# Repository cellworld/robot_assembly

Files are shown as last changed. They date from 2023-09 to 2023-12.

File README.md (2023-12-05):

# Assembly Instructions 

<!-- ![Alt Text](https://github.com/cellworld/robot_assembly/blob/master/robot_overview.png) -->
<p align="center">
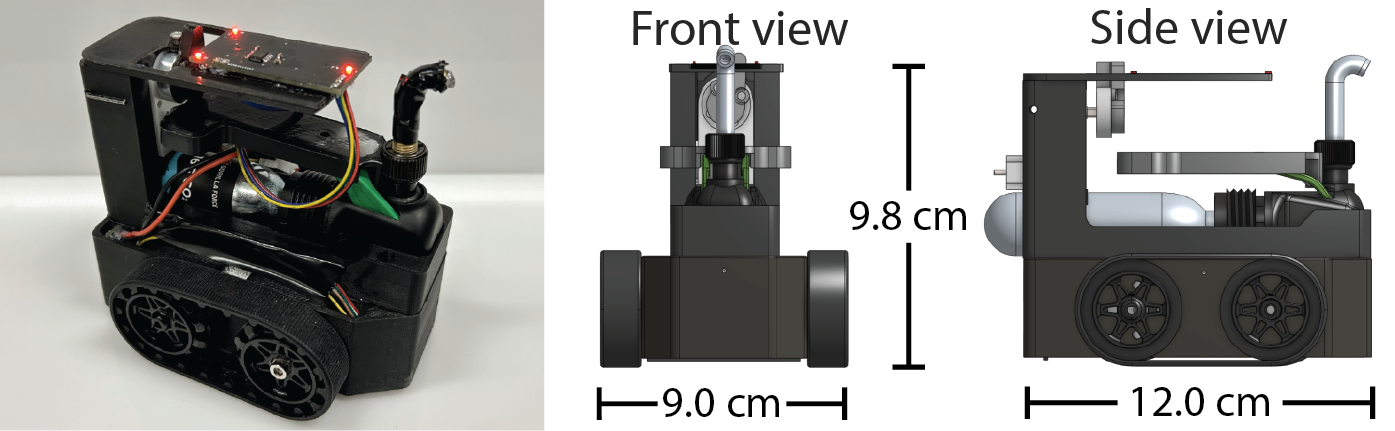
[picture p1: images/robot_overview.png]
robot_overview
  
</p>

## 3D printed parts
* chassis.stl 
* pump_holder.stl
* motor_stopper.stl
* motor_platform.stl
* lever_arm.stl
* cam.stl

## Robot and aversive puff parts
* **Plastic gearmotor** (Gearmotor and Encoder Assembly for Romi/TI-RSLK MAX, Pololu, Las Vegas, Nevada, USA, part no. 3675)
* **Motor shaft adapter** ( Pololu Universal Aluminum Mounting Hub for 3mm Shaft, M3 Holes (2-Pack), Pololu, Las Vegas, Nevada, USA, part no. 1996)
* **Valve stem extender** (2-Pack Tire Valve Extension 45 Degree, LEEGAWU)
* **16g CO2 canister and inflator** (Ultraflate, Genuine Innovations, San Luis Obispo, CA, USA)
* **Drivetrain motor** (Geared DC Motor with Magnetic Encoder Outputs - 7 VDC 1:20 Ratio, Adafruit, New York, NY, USA, part no. 4416)
* **Battery** 7.4V (7.4V 1000mAh Odamiya Plug Lithium Battery, PUOO)
* **Track set** (Pololu 22T Track Set - Black, Pololu, Las Vegas, Nevada, USA, part no. 3030)

## Printed circuit board (PCB) components
<!-- maybe add actual photo of assembled pcbs-->
<p align="center">
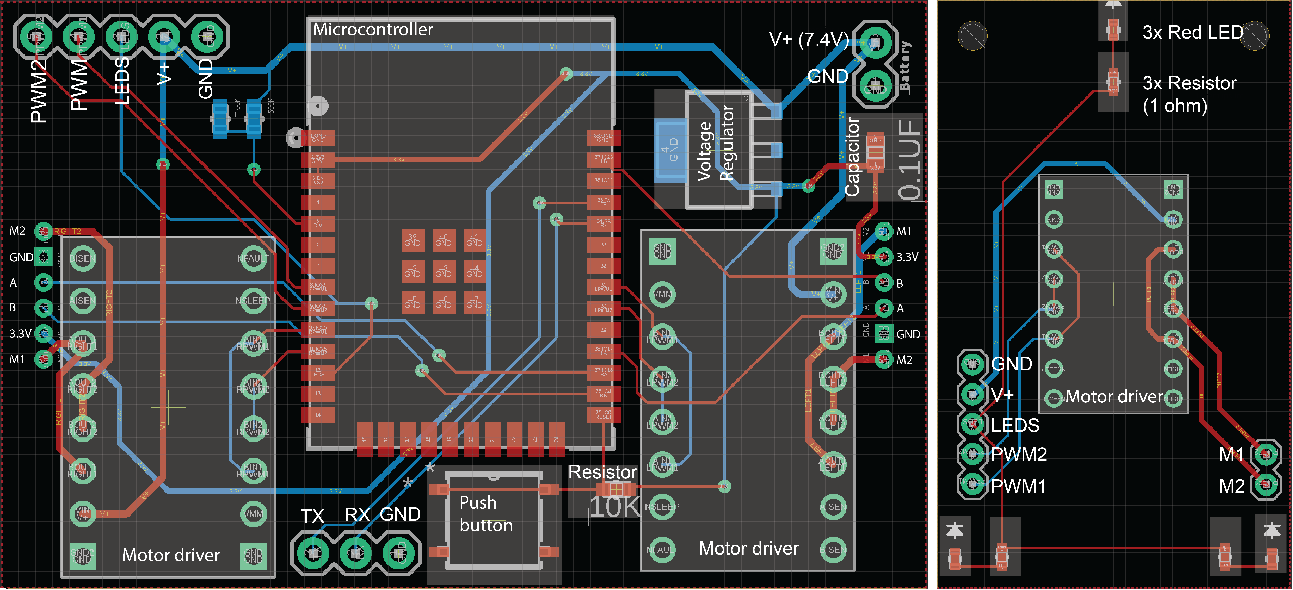
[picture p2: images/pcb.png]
pcb
  
</p>

* **Microcontroller** (ESP32-WROOM-32D, Espressif Systems, Shanghia, Shanghai, China)
* **Motor driver** ( DRV8833 Dual Motor Driver Carrier, Pololu, Las Vegas, Nevada, USA, part no. 2130)
* **Voltage regualtor** (IC REG LIN 3.3V 500MA SOT223-4, Texas Instruments, Dallas, TX, USA, Digi-key part no. 296-13424-1-ND)
* **Resistor** $10K \Omega$ (RES SMD 10K OHM 5% 1/10W 0603)
* **Capacitor** $0.1 \mu F$ (0.1 µF ±20% 50V Ceramic Capacitor X7R 0603 (1608 Metric))
* **Push button** (TACT 5.2 X 5.2, 1.5 MM H, 260GF, C&K, Digi-key part no. CKN12221-6-ND)
* **Red LED** (SMD 0603 (1.6mm x 0.8mm) Red LED Diode, Chanzon)
* **Resistor** $1 \Omega$ (RES 1 OHM 5% 1/4W 0402)
* **Drivetrain motor cable** (6 CIRC PICOBLADE RECP:PLUG 150MM, Molex, Lisle, IL, USA, Digi-key part no. 	900-2181130601-ND)
* **Plastic gearmotor cable** (JUMPER WIRE 0.1" 2-PIN 6", SparkFun Electronics, Niwot, CO, USA, Digi-key part no. 1568-1929-ND)
* **PCB connection cable** (JUMPER WIRE 0.1" 5-PIN 6", SparkFun Electronics, Niwot, CO, USA, Digi-key part no. 1568-1932-ND)

## PCB Assembly
This PCB was design using EAGLE. It is PCB CAD software. EAGLE is available from Autodesk either as part of the Fusion 360 software package or you can a free version of just EAGLE [here](https://www.autodesk.com/products/eagle/free-download). The EAGLE project, associated library, and gerber files are located in the pcb directory [here](https://github.com/cellworld/robot_assembly/tree/master/pcb/).

## Chassis assembly
<p align="center">
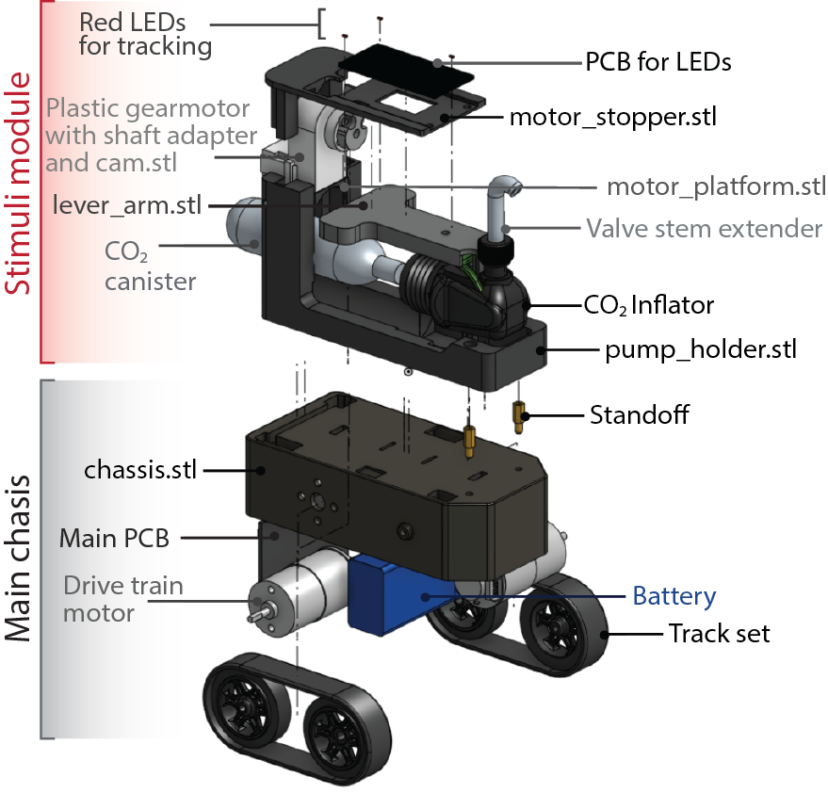
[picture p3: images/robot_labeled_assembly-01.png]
labeled robot
  
</p>

### Main chassis
1. Attach the two ABS idler sprockets from the *track set* to *chassis.stl* with a M3 shoulder bolt with a 5mm threaded portion, a washer, and a bolt.
2. Mount two *drivetrain motors*  to *chassis.stl* with M3 screws
3. Attach the two ABS drive sprockets to the *drivetrain motor* shafts
4. Attach the two silicone tracks
5. Insert the *main PCB* into the back of the *chassis.stl* and connect it to the *drivetrain motors*
6. Insert the *battery* and connect it to the *main pcb*
   
### Stimuli module 
1. Insert two M3 standoffs into the two front through holes in *chassis.stl*
2. Press fit the *pump_holder.stl* onto the standoffs
3. Add the *16g CO2 canister and inflator*  with *lever_arm.stl* press fit onto it
4. Slide components into the back channel on the  *pump_holder.stl*:
   1. *motor_platform.stl*, so that its rounded surface rests against the CO2 canister
   2. *plastic gearmotor* (with *cam.stl*  fixed to it with the *motor shaft adapter*)
   3. *motor_stopper.stl* 
5. Fix the PCB with LEDs on it to the top of the *motor_stopper.stl* and connect it to the *main PCB* and the *plastic gearmotor*
   
# Code
Relevant code for the robot resides in separate repositories.
* OTA programming code: [Link](https://github.com/cellworld/ESP32_OTA_programmer)
* Embedded code for BotEvade task: [Link](https://github.com/cellworld/robot_embedded_code/tree/b2fe92d203f52c9526e03de08260bb5708b2de43)

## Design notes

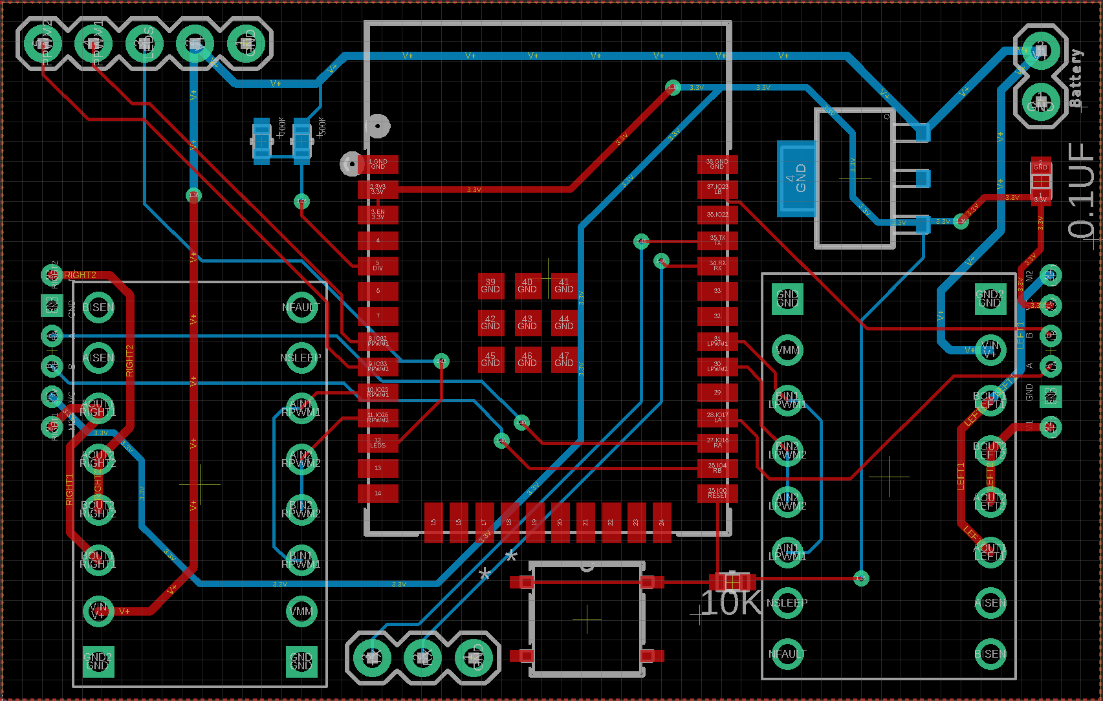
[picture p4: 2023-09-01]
images/main_pcb.png

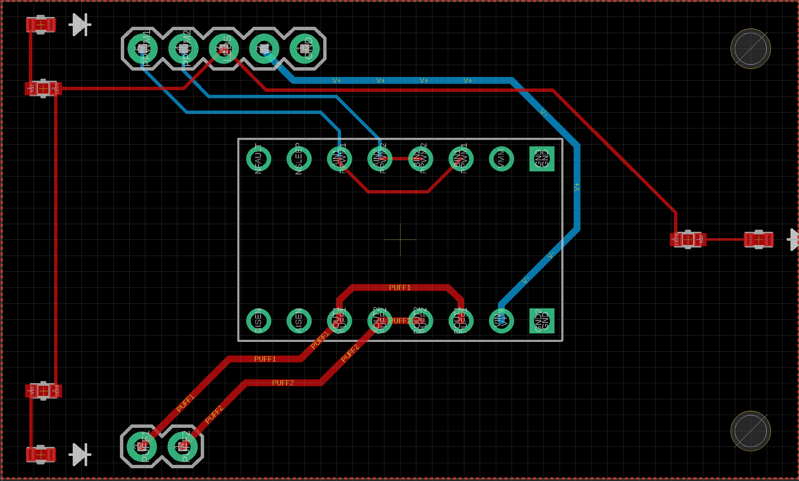
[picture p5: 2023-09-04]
images/top_pcb.png

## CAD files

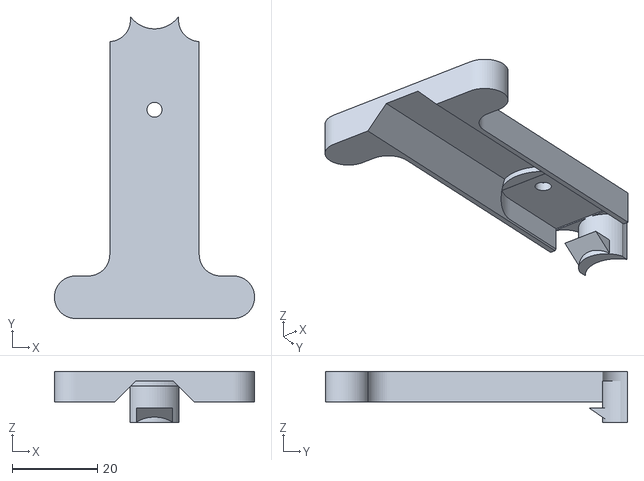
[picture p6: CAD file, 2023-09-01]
3D_printed_parts/lever_arm.stl
47.0 x 70.9 x 12.0

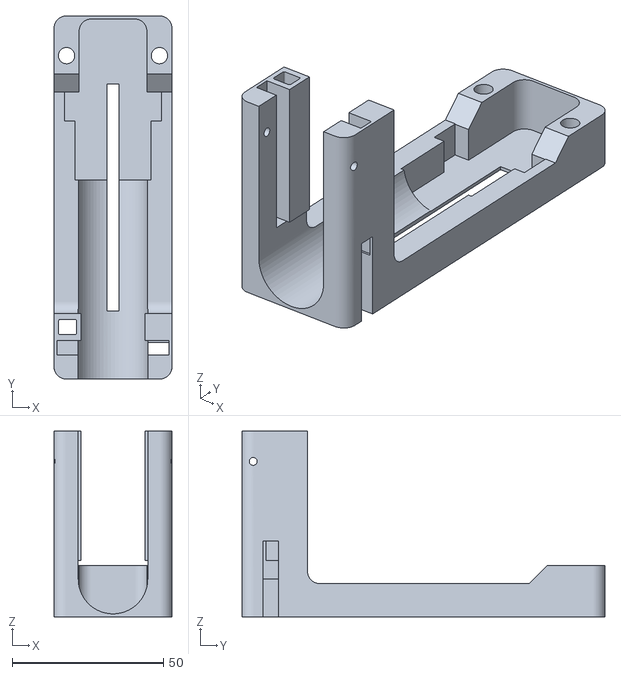
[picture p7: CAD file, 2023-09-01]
3D_printed_parts/pump_holder.stl
39.0 x 120.0 x 61.4

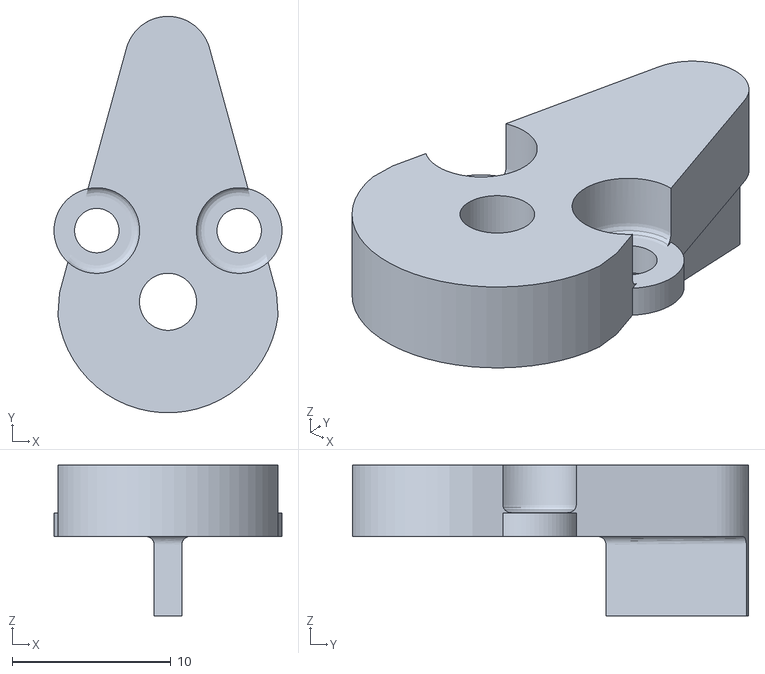
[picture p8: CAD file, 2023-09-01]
3D_printed_parts/cam.stl
14.4 x 25.0 x 9.50

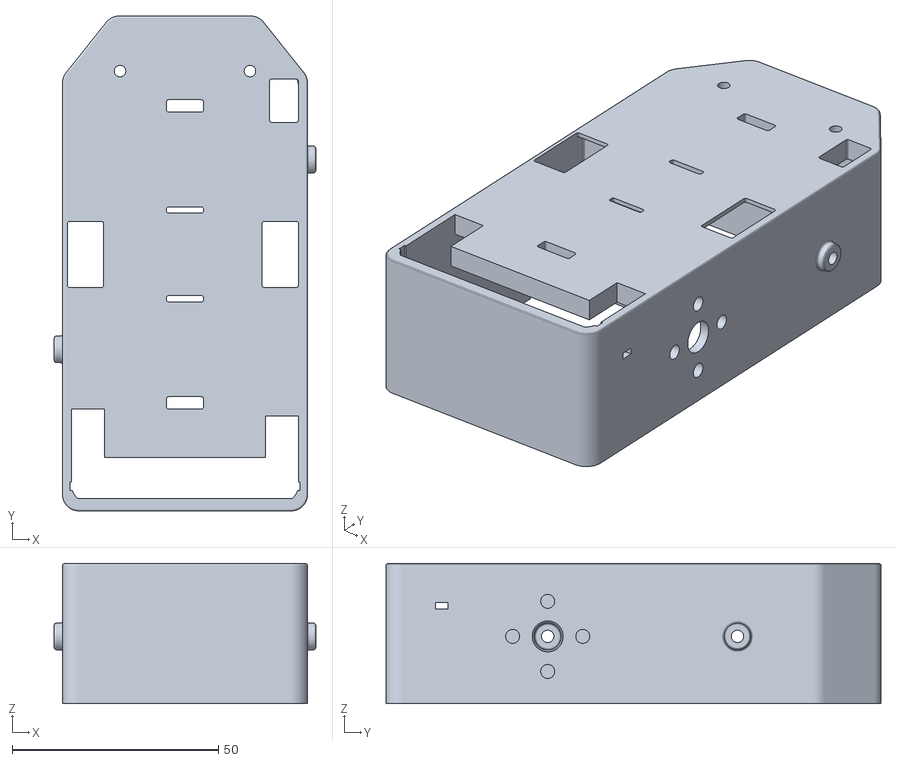
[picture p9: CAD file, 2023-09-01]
3D_printed_parts/chassis.stl
63.4 x 120.0 x 34.0

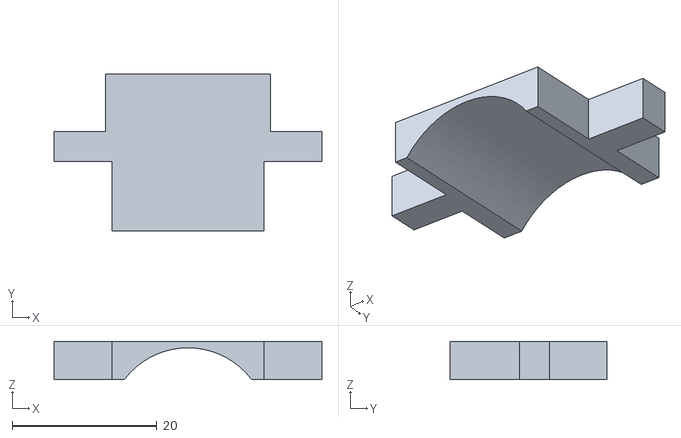
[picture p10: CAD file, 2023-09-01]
3D_printed_parts/motor_platform.stl
37.0 x 21.7 x 5.30

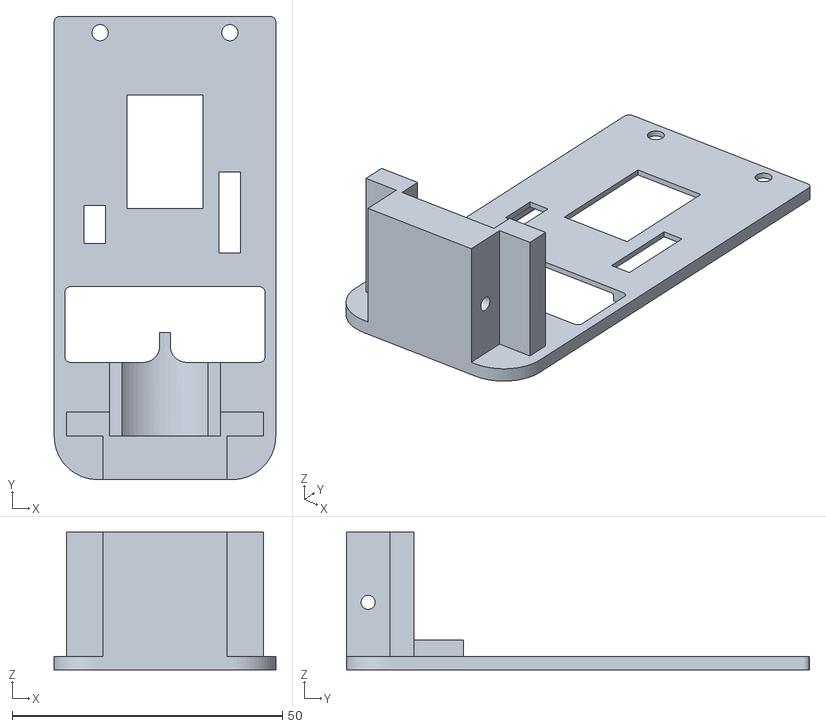
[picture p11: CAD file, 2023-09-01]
3D_printed_parts/motor_stopper.stl
41.0 x 85.7 x 25.5

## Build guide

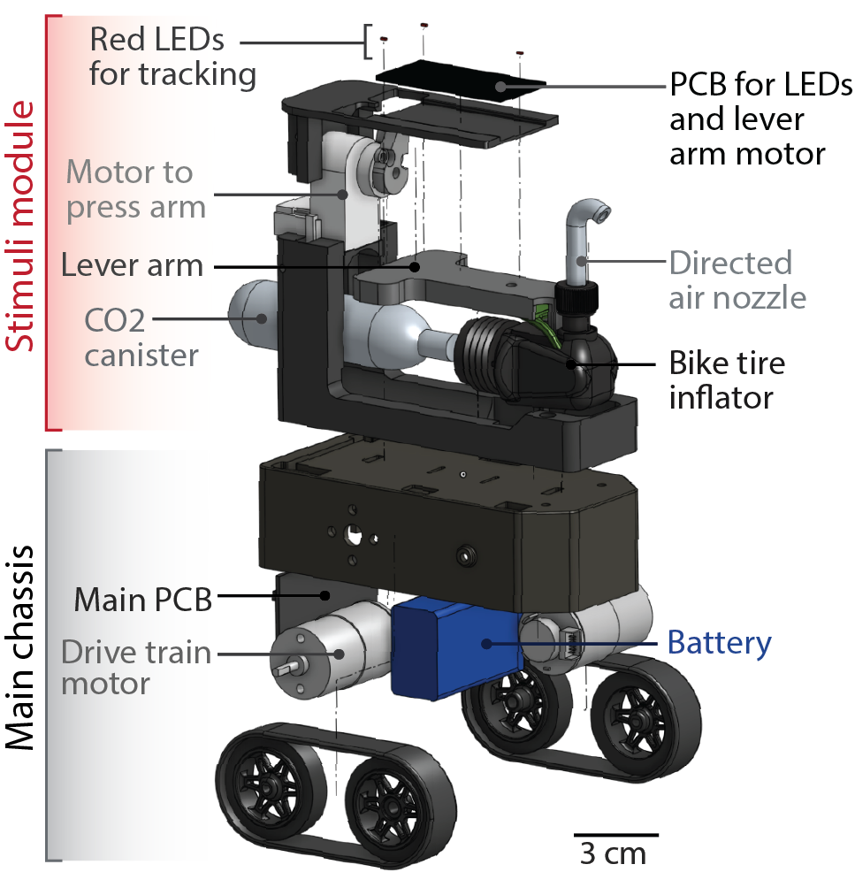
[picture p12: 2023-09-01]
images/robot_assembly.png

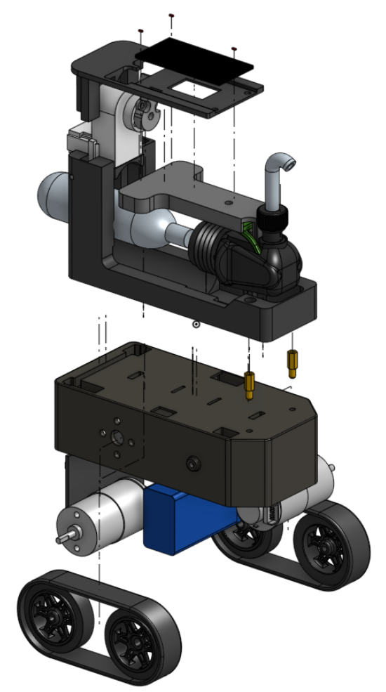
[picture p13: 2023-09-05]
images/assembly.png

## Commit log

2023-09-01 added pcb files
2023-09-01 added all cad files
    [cam.stl, chassis.stl, lever_arm.stl, motor_platform.stl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]
2023-09-04 added pcb image
2023-09-05 main chassis assembly instructions
2023-09-05 assembly instructions updated
2023-09-06 added pcb assmbly instruct
